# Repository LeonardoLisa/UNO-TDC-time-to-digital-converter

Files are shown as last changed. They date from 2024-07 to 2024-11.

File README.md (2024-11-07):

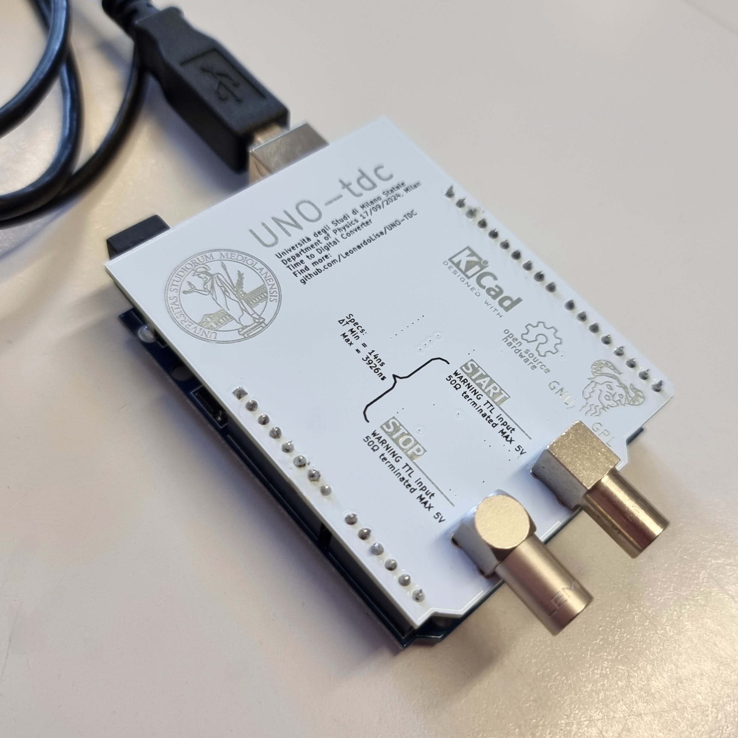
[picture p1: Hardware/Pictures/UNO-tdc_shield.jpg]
UNO-TDC Time to Digital Converter TDC Arduino shield


<h4 align="center">Be sure to :star: my repo so you can keep up to date on any progress!</h4>

## About
The UNO-TDC is a Time to Digital Converter (TDC) that performs the function of a stopwatch and measures the elapsed time between a START pulse and up to five STOP pulses.
The UNO-TDC is a cheap effective acquisition system for nuclear physics experiments. It can be built using off the shelf component like an Arduino UNO and a Texas Instruments TDC7200.

## Specifications overview
The UNO-TDC has a measurement range of 14ns to 3926ns, and a dead time of 100us between two consecutive measurements. UNO-TDC must always receive a STOP signal because it does not feature a STOP timeout. The measurement resolution is 55ps and the error varies according to the measurement range as described in the "UNO-TDC datasheet". As a "rule of thumb" 1% error could be considered on all ranges. The data is not saved but continuously streamed to the computer on the serial port.

## License
This repository uses a complex multilicense system 
- All shared materials in the Hardware directory are shared under the [Creative Commons BY-NC-SA 4](https://creativecommons.org/licenses/by-nc-sa/4.0/deed.en) license.  
- All software in the `\Software` directory is shared under [GPLv3](https://www.gnu.org/licenses/quick-guide-gplv3.html) the license.

## Installation
### Hardware
The hardware is custom made and you have to build it your self. However, it is an opensource project so all production files are available! There are two options: hand soldering all the components following the provided schematic or contact your favorite pcb manifacturer and order the necessary circuit board using the gerbers file under the `\Hardware\Production` directory. If you aim to have your UNO-tdc shield assembled as well, the assembly file and the bill of materials (BOM), are available under the `\Hardware` directory. In the future it may be possible to directly buy a fully tested and assembled board.
Warning: the current implementations use a 16 MHz frequency reference while the Texas Instruments TDC7200EVM evaluation board uses a 8 MHz voltage frequency reference.

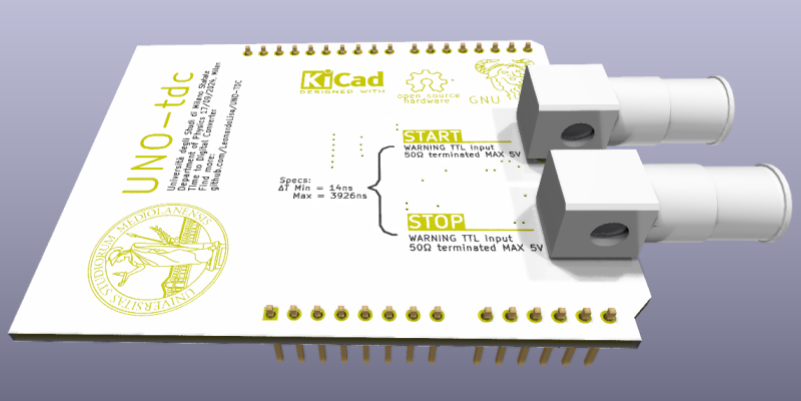
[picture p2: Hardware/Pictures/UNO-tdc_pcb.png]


### Firmware
The firmware can be directly flashed on the Arduino using the Arduino IDE or with an external programmer.
At compilation time it is possible to choose between three data output formats:
1. Prints only the data cointained in the measurement registers (recommended). Comment line 37 and 38.
2. Prints data cointained in the measurement registers, and the registers' names. Only comment line 37.
3. Prints the time of flight computed by the Arduino UNO (not recommended). Only comment line 38.
These are the snippets of code that have to be changed in order to select the data ouput format:

```cpp
/* Data format option */
#define EASYDATA
//#define RAWDATA
```

Please note that the Arduino UNO is based on the Atmega328-PB which is an 8 bit AVR microcontroller that doesn't natively support floting point operations. Therefore calculating the time of flight at runtime uses a lot of resouces and may lead to data loss due to full measurement serial buffer. The Arduino will inform you using a message when a measurement is lost. This is the reason why using option 1 is recommended.

With regards to option 3, the measurement values are calculated according to a 16 MHz frequency reference. In order to use a 8 MHz frequency reference line 170 has to be changed to:

```cpp
Serial.println((rawTime * 1125) / Difference);
```

### Data Parser
The data parser is needed only if you have compiled the firmware using option 1 or 2. The data parser has be compiled so you must have already install a C++ compiler. 

```console
make
```

Right now it is only compatible with Linux machines. The measurement values are calculated according to a 16 MHz frequency reference. If you are using a 8 MHz frequency reference line 207 has to be changed to:

```cpp
tof = (rawMeasurement.time * 1125) / calcount;
```

## Usage
### Acquiring data
1. Before starting the data acquisition the serial port on your computer must be configured as follows:
- Parity = no parity bit
- Baud rate = 38400 

2. Connect the UNO-TDC to your computer and open the serial port with the console or any other software of your choice. For convenience you may want to use a data logging program like Rufus. On Arduino IDE simply open the serial monitor.

3. To start the data acquisition the UNO-TDC must receive a character or a string on the serial port from the computer.

4. When the acquisition begins a start up message will appear on the serial port and will start to continuously stream.


5. To interrupt the measurement session close the serial port and disconnect the UNO-TDC from the computer. 

### Parsing Data
The data parser is needed only if you have compiled the firmware using option 1 or 2. The data parsing software is a console program, it can be run as follows.

```console
.\main data_filename 3700
```
It expects 2 parameters:
- data_filename: the raw log output from UNO-TDC.
- stop_limit: upper limit in nanoseconds, where any longer measurements will be ignored.

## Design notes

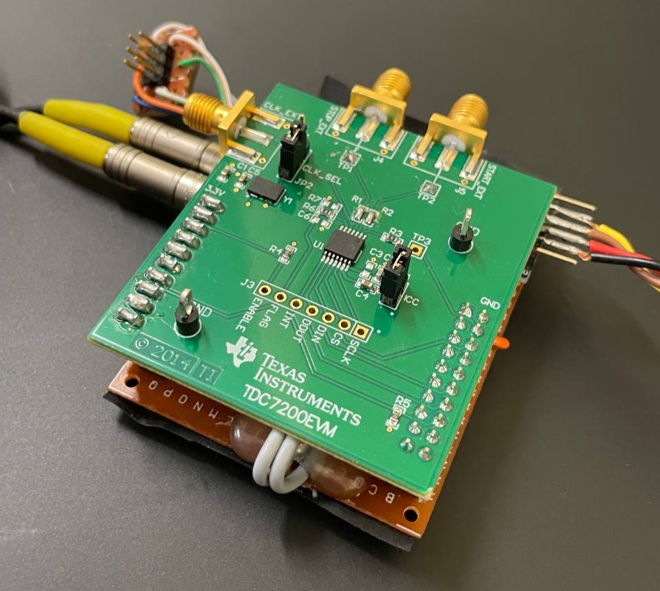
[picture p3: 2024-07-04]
Hardware/Pictures/tdc_img.jpg

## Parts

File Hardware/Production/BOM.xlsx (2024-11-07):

Item # | *Designator | *Qty | *Mfg Part # | Description / Value | *Package/Footprint | Mounting Type
1 | A1 | 1 |  | Arduino_UNO_R3 Arduino UNO Microcontroller Module, release 3 | Arduino_UNO_R3 | tht
2 | C1, C5, C6 | 3 | 0603YC104JAT2A | 100n CAP, CERM, 0.1uF, 16V, +/-5%, X7R, 0603 | C_0603_1608Metric | smt
3 | C2, C4 | 2 | 06031C103JAT2A | 10n CAP, CERM, 0.01uF, 100V, +/-5%, X7R, 0603 | C_0603_1608Metric | smt
4 | C3 | 1 | EMK107B7105KA-T | 1u CAP, CERM, 1uF, 16V, +/-10%, X7R, 0603 | C_0603_1608Metric | smt
5 | D1, D2 | 2 | GG0402050R8L2P | D_TVS 5V Bidirectional transient-voltage-suppression diode | D_0402_1005Metric | smt
6 | J1 | 1 | EPL.00.250.NTN | START coaxial connector LEMO right angle | SMA_Amphenol_901-143_Horizontal | tht
7 | J2 | 1 | EPL.00.250.NTN | STOP coaxial connector LEMO right angle | SMA_Amphenol_901-143_Horizontal | tht
12 | R1, R2 | 2 | CRCW060349R9FKEA | 50R RES, 49.9 ohm, 1%, 0.1W, 0603 | R_0603_1608Metric | smt
13 | R3 | 1 | CRCW06031K00FKEA | 1k RES, 1.00k ohm, 1%, 0.1W, 0603 | R_0603_1608Metric | smt
14 | U1 | 1 | TDC7200PWR | TDC7200 Serial Time to Digital Converter | TSSOP-14_4.4x5mm_P0.65mm | smt
15 | U2 | 1 | TXB0108PWR | TXB0108PW 8-Bit Bidirectional Voltage-Level Translator | TSSOP-20_4.4x6.5mm_P0.65mm | smt
16 | U4 | 1 | ASFLMB-16.000MHZ-LY-T | ASFLMB-16.000MHZ OSC, 16MHz, 15pF, SMD 3.2x.85x5mm | ASFLMB-XXMHZ-LY-T | smt

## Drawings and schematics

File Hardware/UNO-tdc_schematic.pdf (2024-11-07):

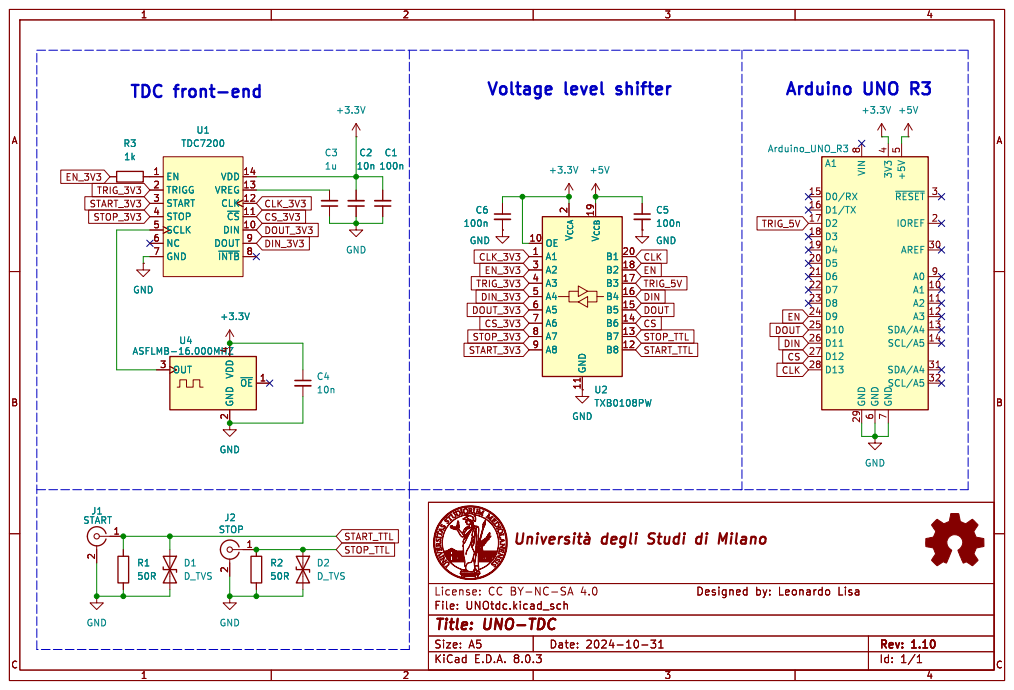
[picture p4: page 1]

~{RESET}3 AREF 30 SDA/A4 31 SCL/A5 32 3V3

A1 10 A2 11 A3 12 SDA/A4 13 SCL/A5 14 D0/RX 15 D1/TX 16 D2 17 D3 18 D4 19

File: UNOtdc.kicad_sch
Id: 1/1 Title: UNO-TDC
